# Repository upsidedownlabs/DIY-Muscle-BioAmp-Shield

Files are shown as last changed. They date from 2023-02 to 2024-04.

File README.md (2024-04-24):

# Muscle BioAmp Shield

 


[]()



Muscle BioAmp Shield is an all-in-one Arduino Uno ElectroMyography (EMG) shield for learning neuroscience with ease. It is a DIY Electrophysiology/NeuroScience shield inspired from Back Yard Brains (BYB) Muscle Spiker shield and provides similar features like hobby servo output, user buttons, LED Bar, Audio output, and battery input. It is perfect for beginners as they can easily stack it on top of Arduino Uno to record, visualize and listen to their muscle signals to make amazing projects in the domain of Human-Computer Interface (HCI).

## Features & Specifications

Muscle BioAmp Shield comes with various plug-and-play options so you can connect hundreds of extension boards like OLED screens, character displays, accelerometers, and servo controllers to name just a few using the STEMMA I2C interface. You also get STEMMA digital and STEMMA analog ports. On STEMMA analog port you can connect additional [BioAmp EXG Pill](https://github.com/upsidedownlabs/BioAmp-EXG-Pill) or any other sensor with analog output. On STEMMA digital port you can connect any digital sensor or actuator of your choice.

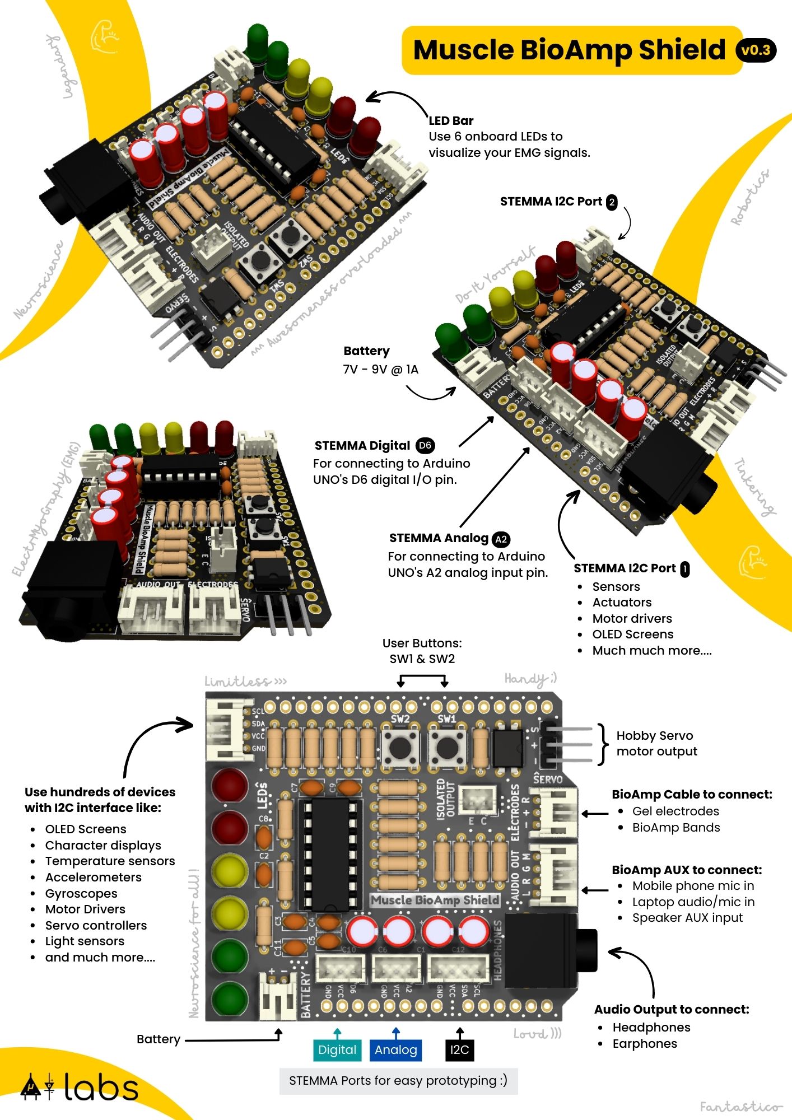
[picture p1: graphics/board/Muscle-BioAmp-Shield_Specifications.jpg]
Muscle BioAmp Shield Specifications


## Assembly
You can get your own Muscle BioAmp Shield bag of parts from [our store](https://store.upsidedownlabs.tech/product/muscle-bioamp-shield-v0-3/) or [Tindie](www.tindie.com/products/upsidedownlabs/muscle-bioamp-shield-v03-arduino-shield-for-emg/) and for assembling your shield you can take a look at [this interactive BOM](https://upsidedownlabs.github.io/DIY-Muscle-BioAmp-Shield/ibom.html) or the step by step guide below. 

| Step 1 - Bare board | Step 2 - 1M Resistors | Step 3 - 330R Resistors| 
| :----: | :----: | :----: |
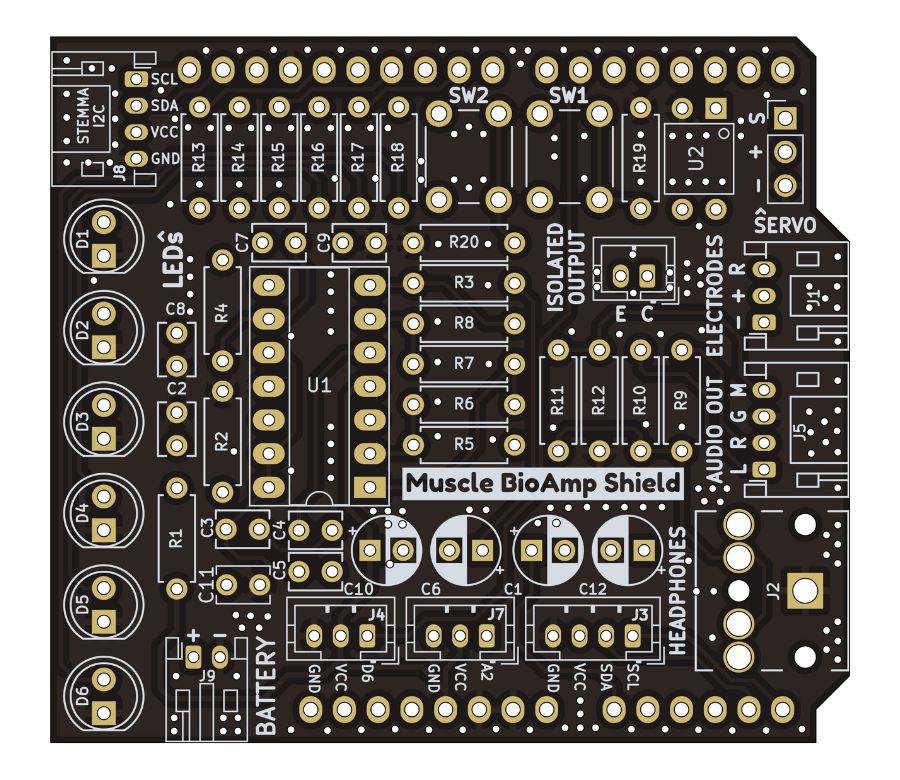
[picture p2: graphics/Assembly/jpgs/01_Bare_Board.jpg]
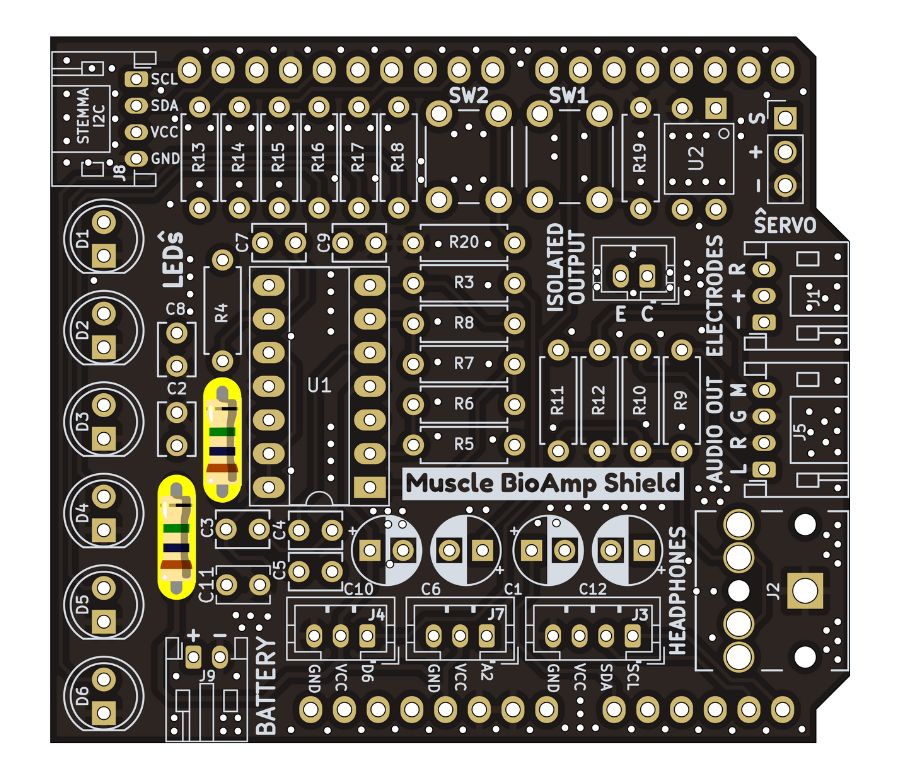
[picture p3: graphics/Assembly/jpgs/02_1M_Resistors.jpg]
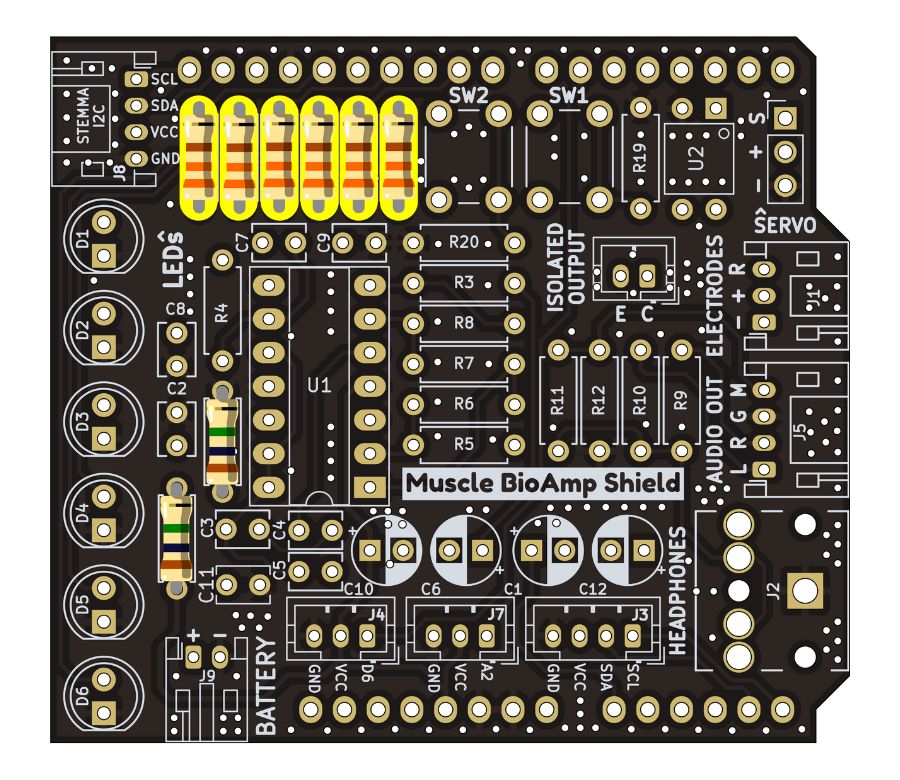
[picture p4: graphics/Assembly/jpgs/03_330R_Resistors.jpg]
| |||

| Step 4 - 10K Resistors | Step 5 - 22K Resistors | Step 6 - 1K Resistors| 
| :----: | :----: | :----: |
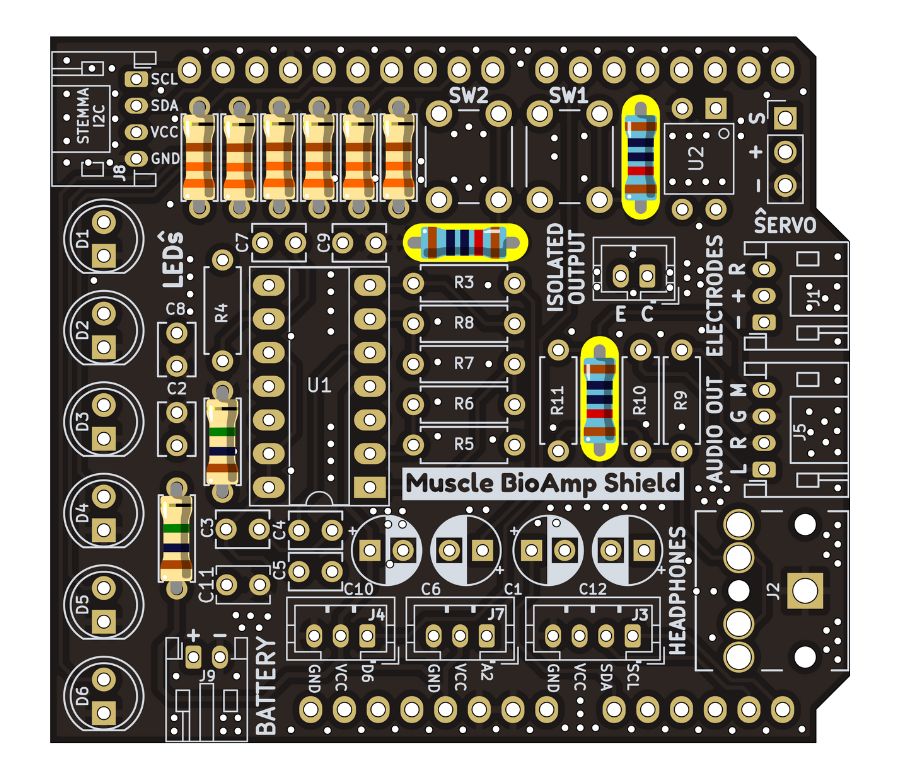
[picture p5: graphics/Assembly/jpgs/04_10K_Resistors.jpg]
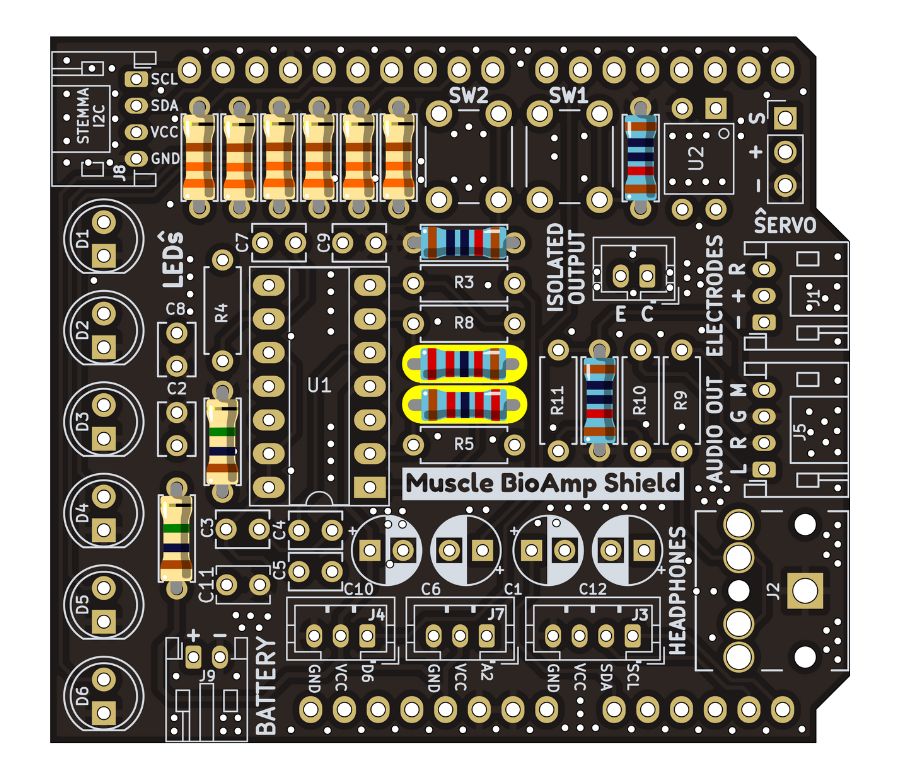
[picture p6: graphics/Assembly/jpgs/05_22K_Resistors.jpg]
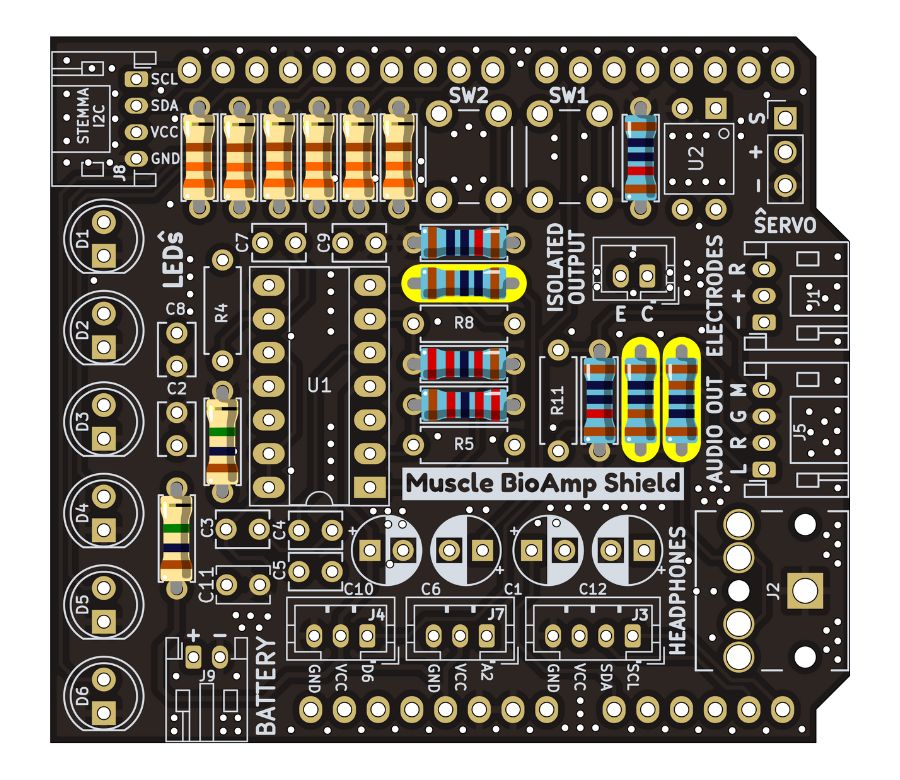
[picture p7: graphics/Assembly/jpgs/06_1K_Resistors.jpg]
| |||

| Step 7 - 220K Resistors | Step 8 - 1nF Capacitors | Step 9 - 100nF Capacitors| 
| :----: | :----: | :----: |
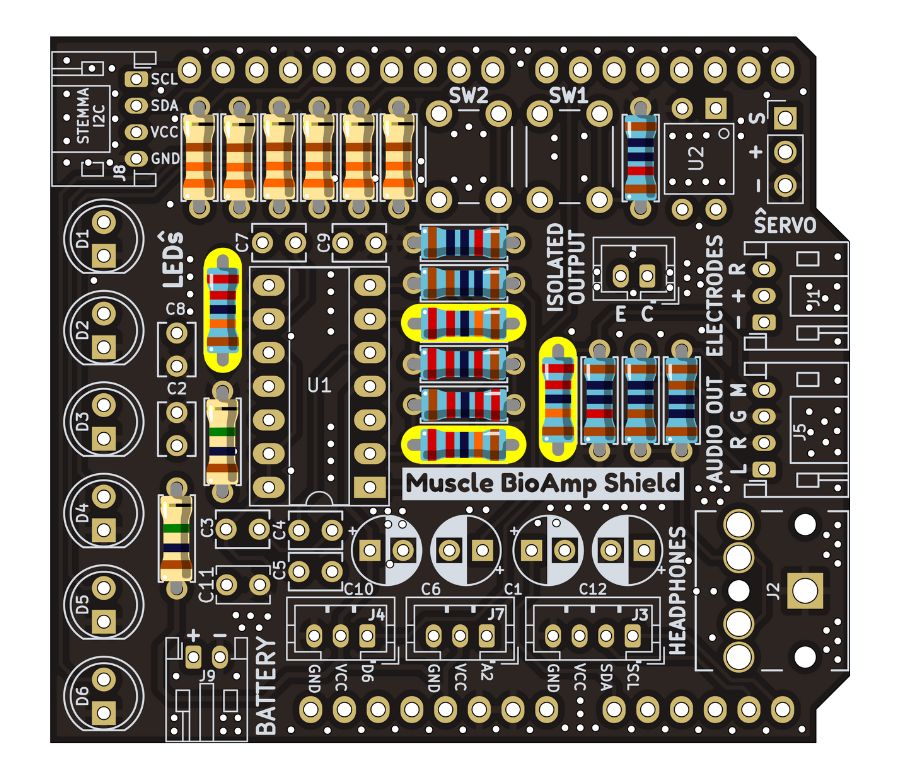
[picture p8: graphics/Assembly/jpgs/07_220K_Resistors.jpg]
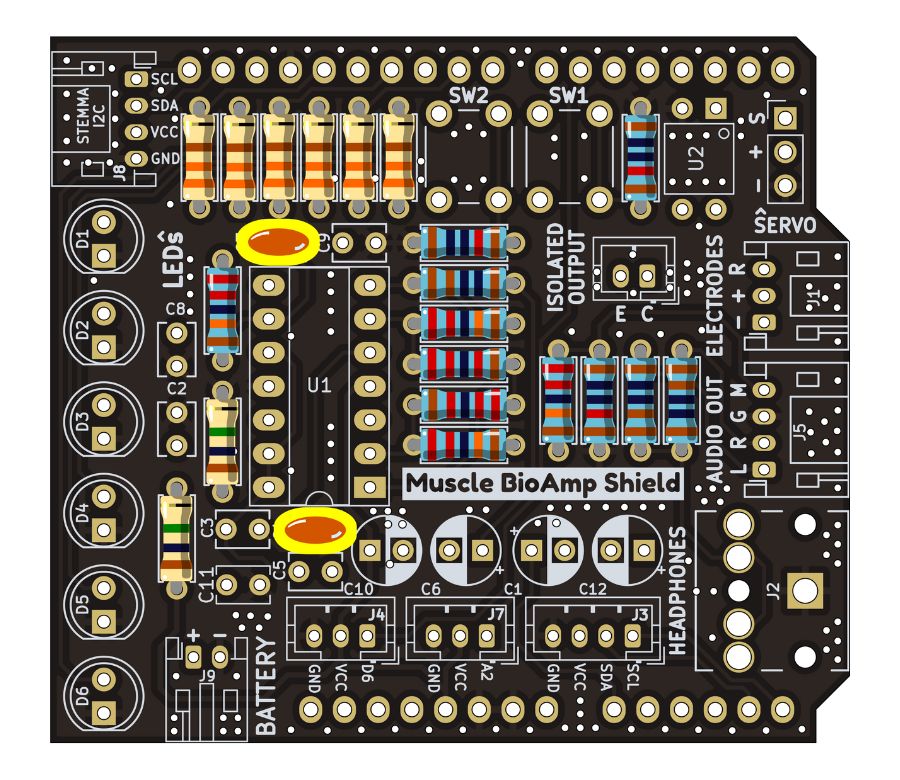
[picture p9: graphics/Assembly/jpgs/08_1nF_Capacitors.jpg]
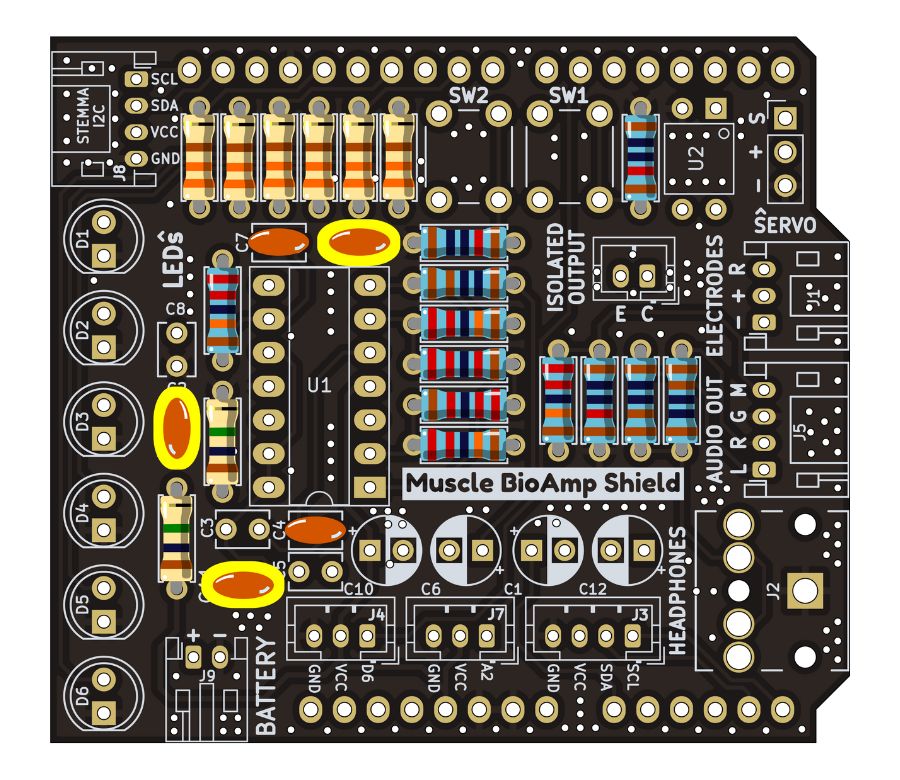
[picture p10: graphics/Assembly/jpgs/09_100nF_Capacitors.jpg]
| |||

| Step 10 - 100pF Capacitors | Step 11 - Servo Header Pin | Step 12 - Buttons| 
| :----: | :----: | :----: |
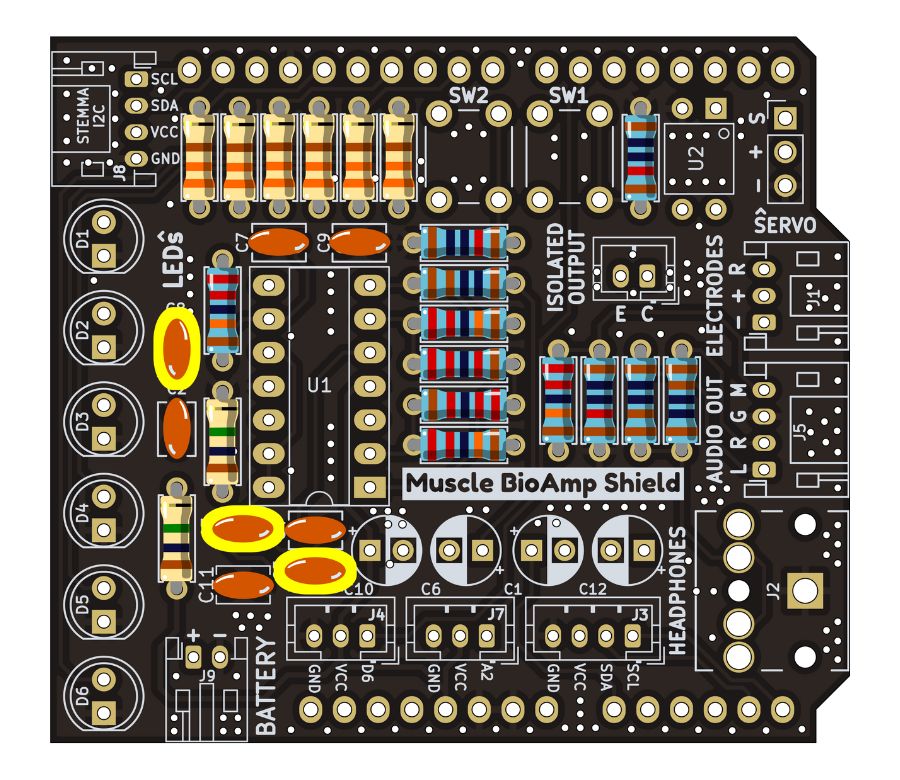
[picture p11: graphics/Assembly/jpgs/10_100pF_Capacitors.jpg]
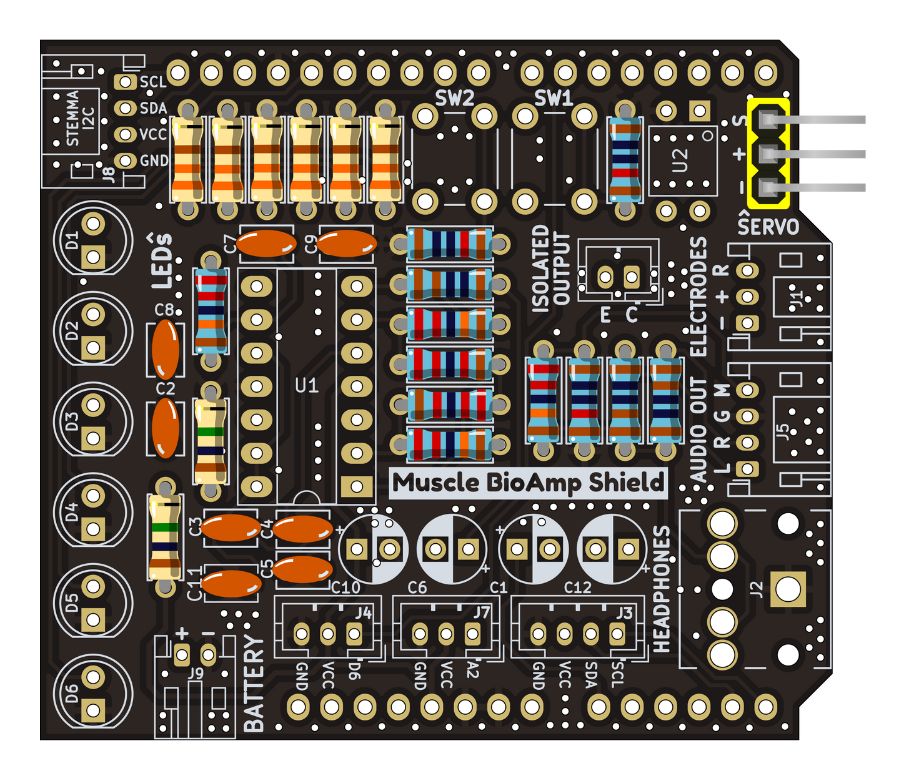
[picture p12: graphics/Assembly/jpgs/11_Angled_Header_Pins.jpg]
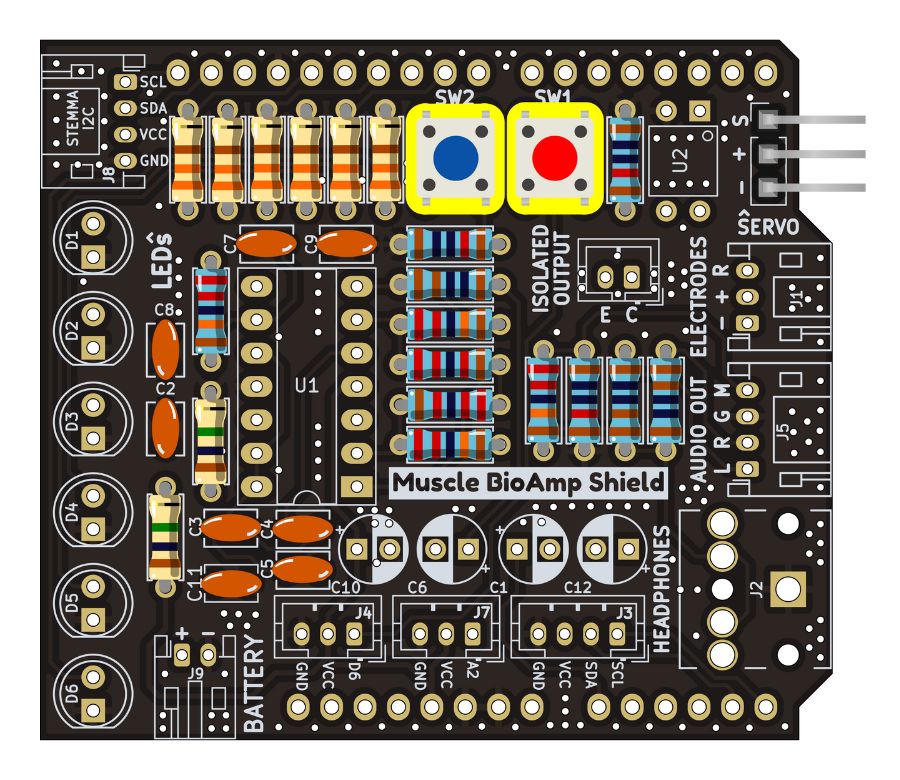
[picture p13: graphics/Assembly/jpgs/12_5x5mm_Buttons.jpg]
| |||

| Step 13 - Optoisolator | Step 14 - Angled JST Connectors | Step 15 - Straight JST Connectors| 
| :----: | :----: | :----: |
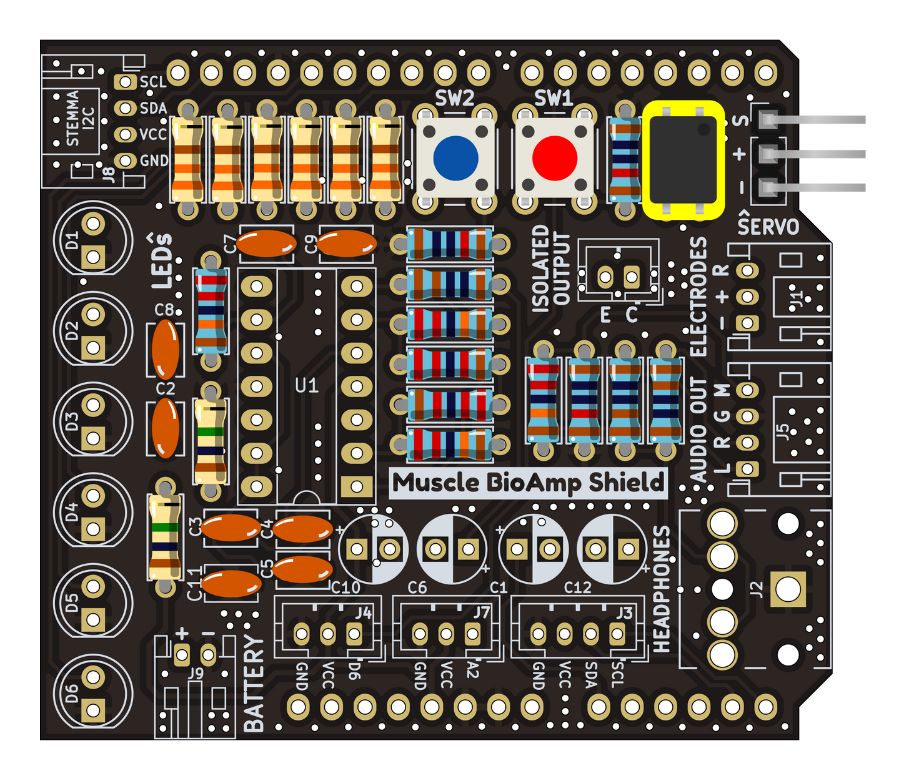
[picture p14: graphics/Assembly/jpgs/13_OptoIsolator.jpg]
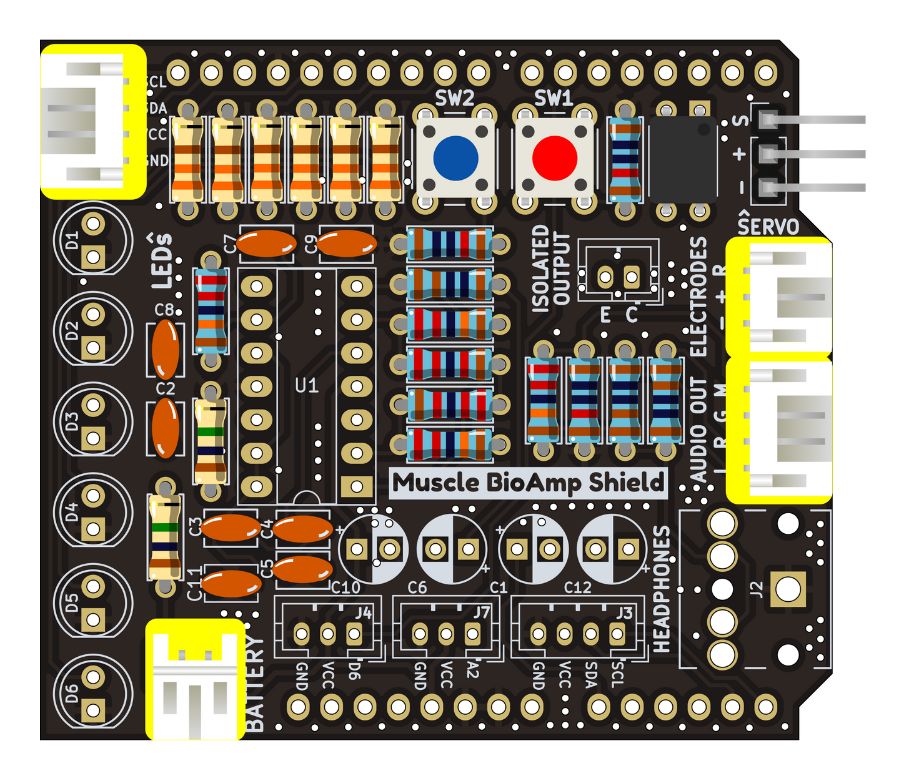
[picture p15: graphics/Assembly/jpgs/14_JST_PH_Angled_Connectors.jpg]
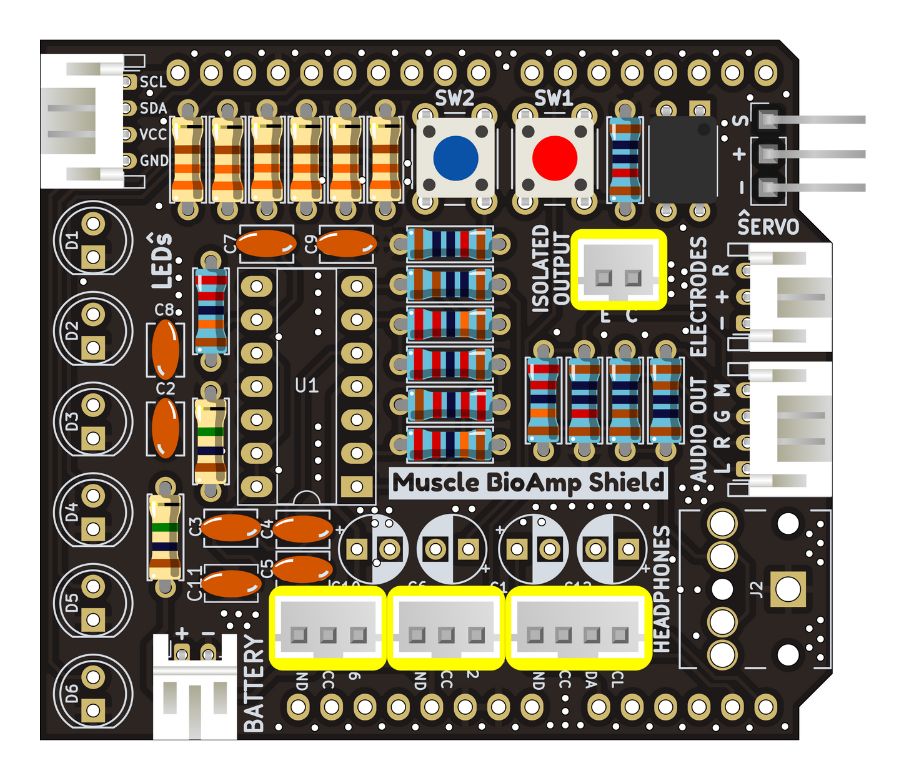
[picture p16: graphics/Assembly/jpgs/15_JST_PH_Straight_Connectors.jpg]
| |||

| Step 16 - IC Socket | Step 17 - IC | Step 18 - LEDs| 
| :----: | :----: | :----: |
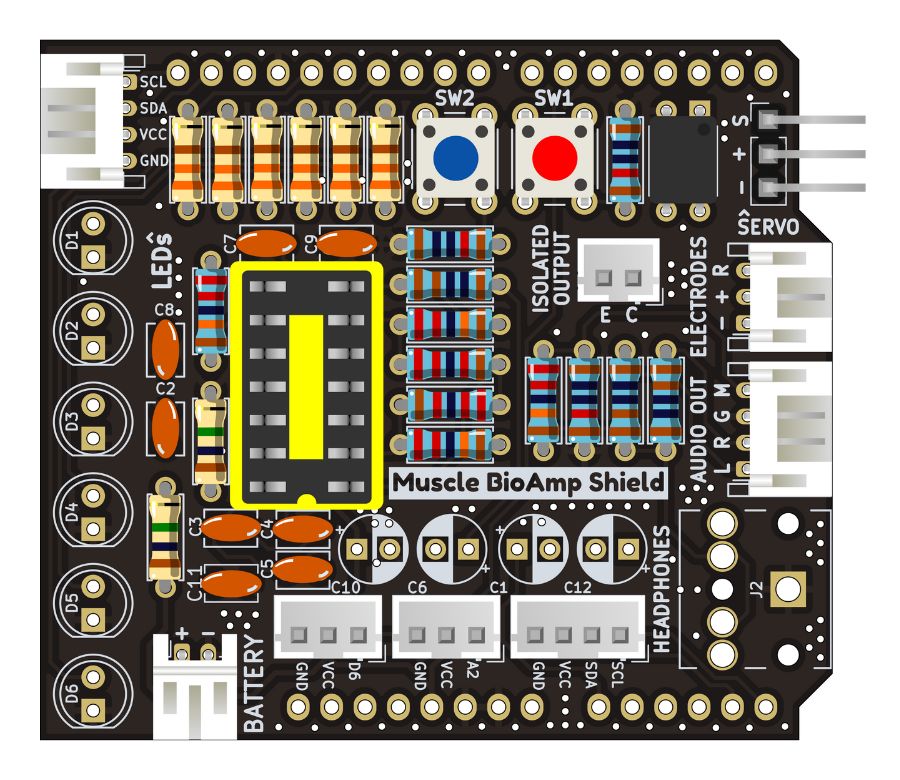
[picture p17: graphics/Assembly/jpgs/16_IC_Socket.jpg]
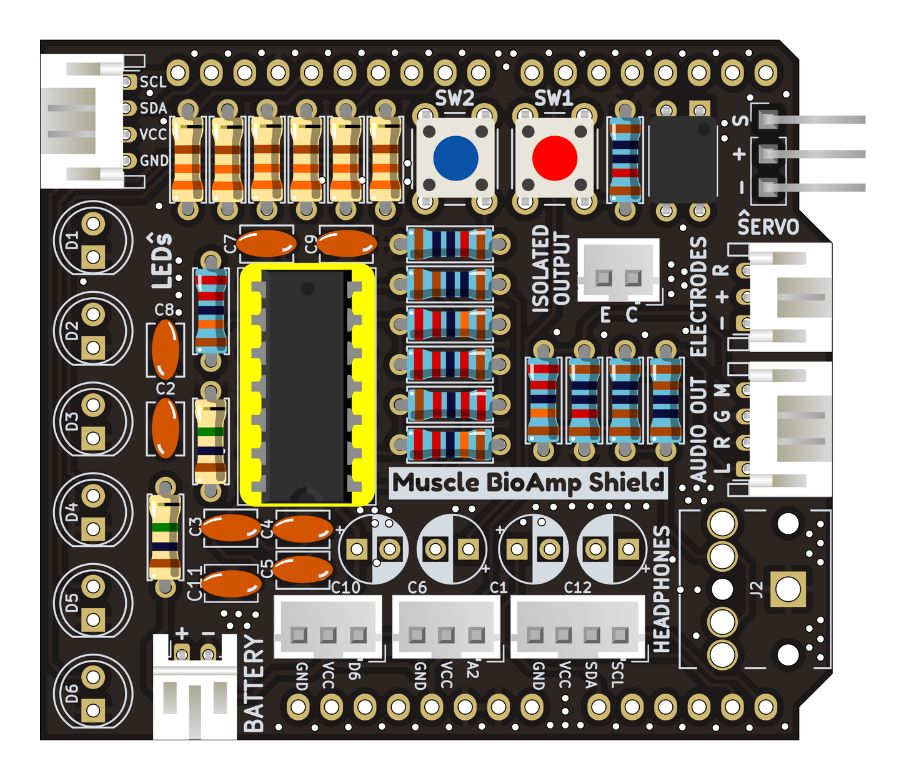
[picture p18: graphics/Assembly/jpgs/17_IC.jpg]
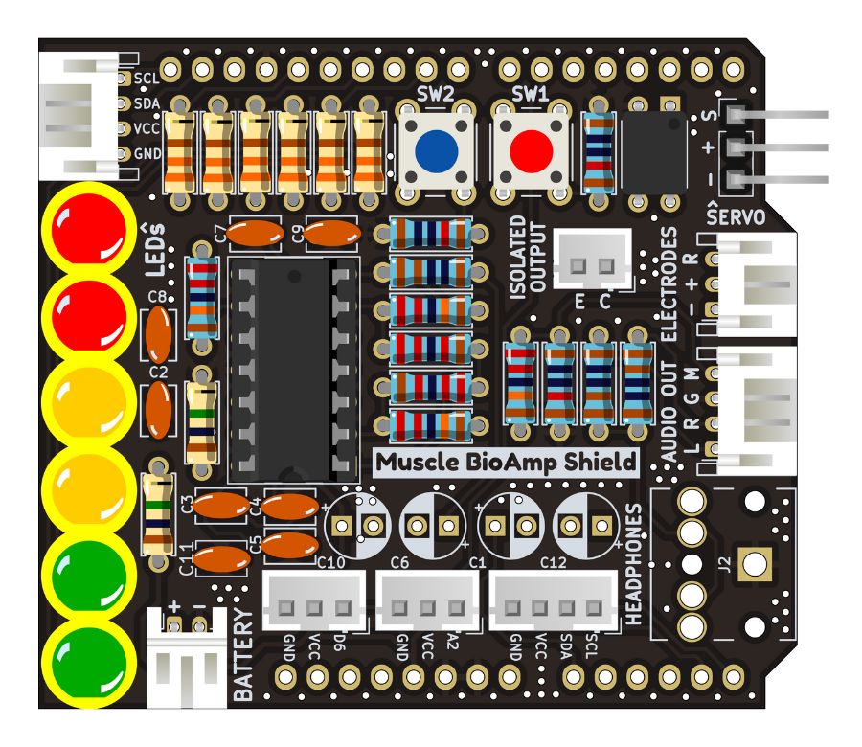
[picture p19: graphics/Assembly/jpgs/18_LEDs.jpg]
| |||

| Step 19 - 3.5mm Headphone Jack | Step 20 - 2.2uF Capacitor | Step 21 - 1uF Capacitor| 
| :----: | :----: | :----: |
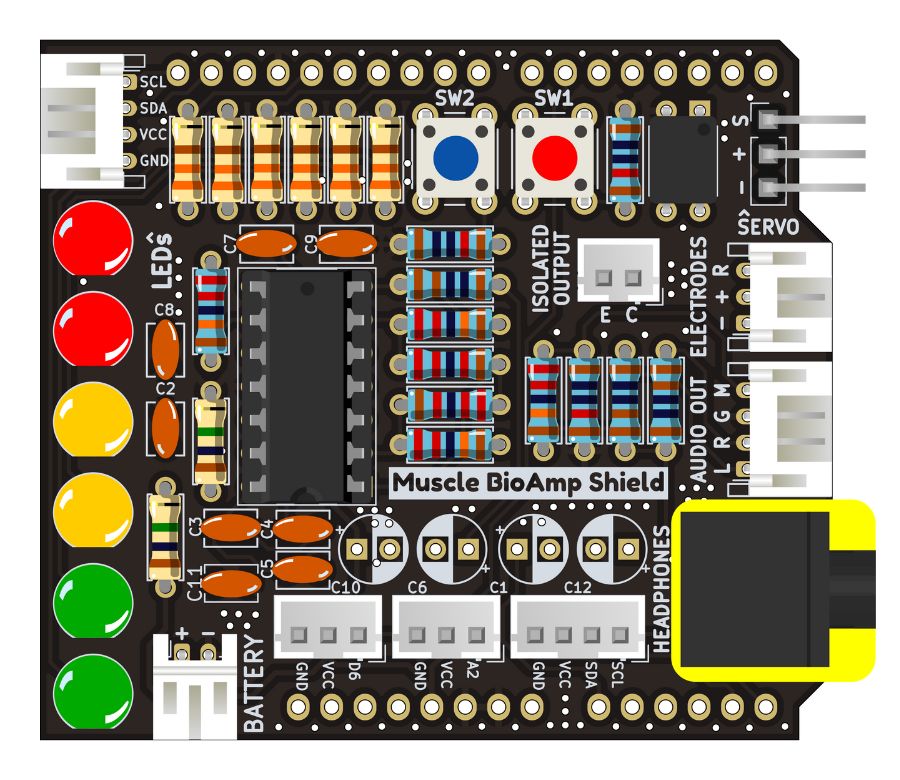
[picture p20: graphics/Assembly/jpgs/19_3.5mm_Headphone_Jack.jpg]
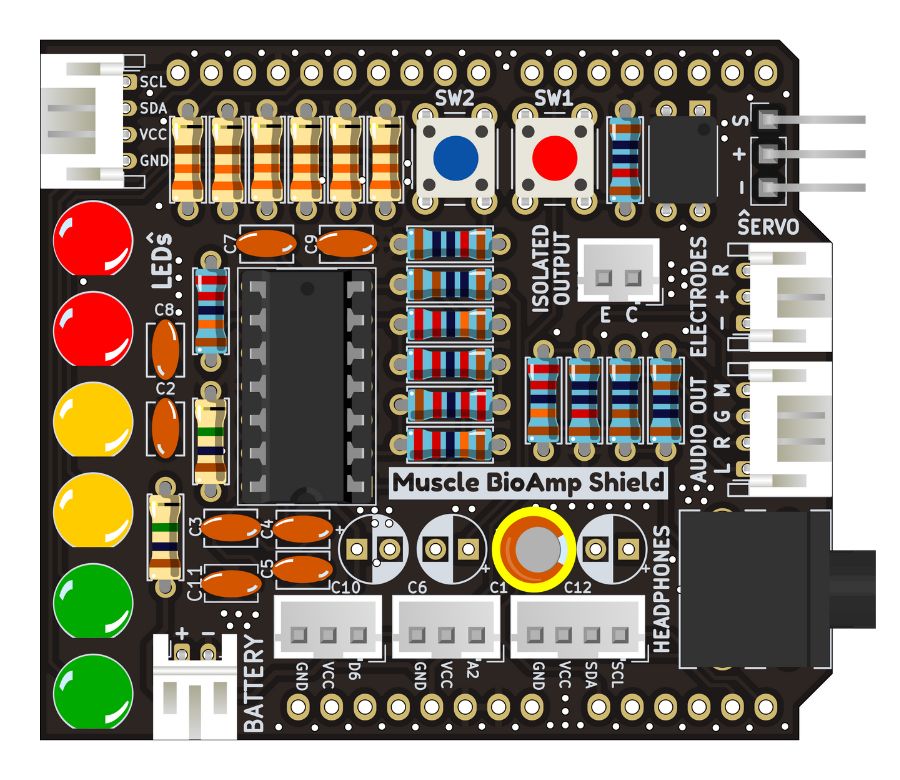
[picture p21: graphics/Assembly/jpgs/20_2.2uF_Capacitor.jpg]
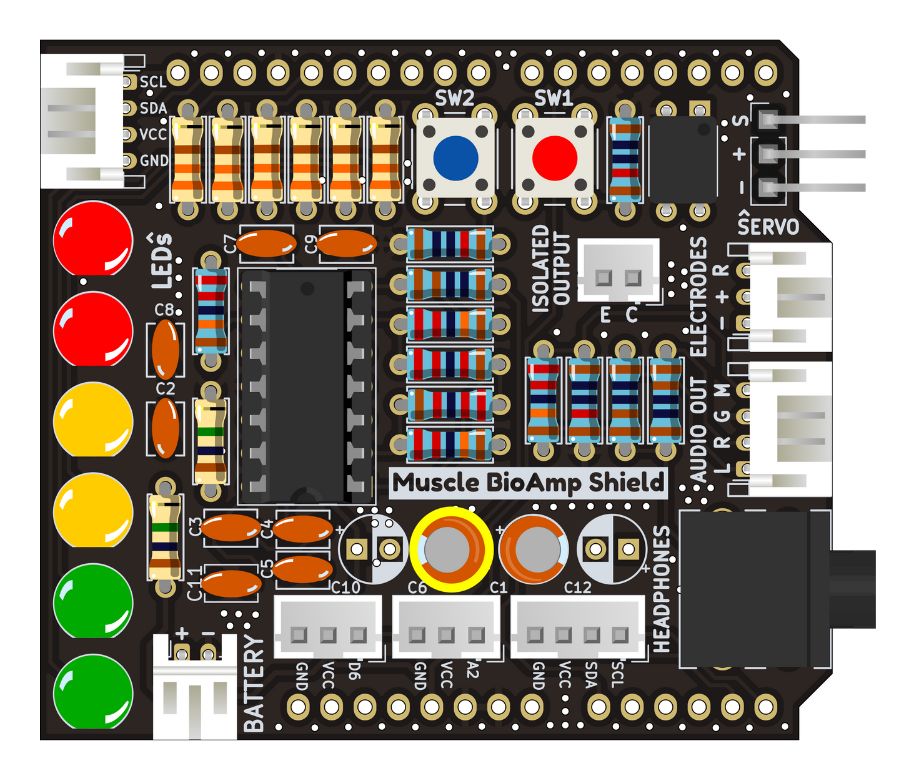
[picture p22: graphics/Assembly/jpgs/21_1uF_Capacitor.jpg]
| |||

| Step 22 - 470uF Capacitors | Step 23 - Shield Header Pins | Step 24 - Shield Ready| 
| :----: | :----: | :----: |
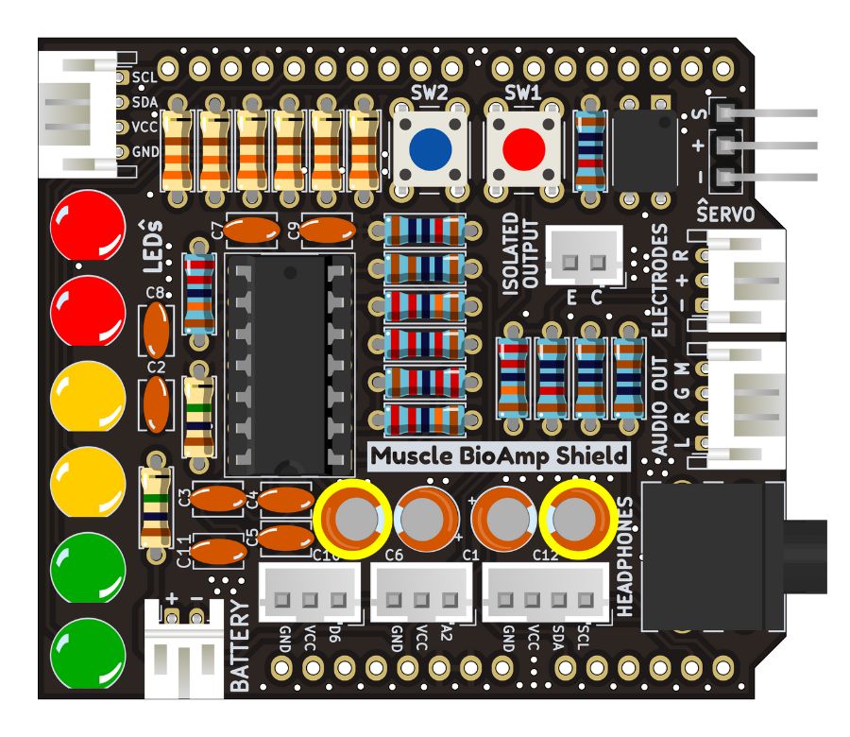
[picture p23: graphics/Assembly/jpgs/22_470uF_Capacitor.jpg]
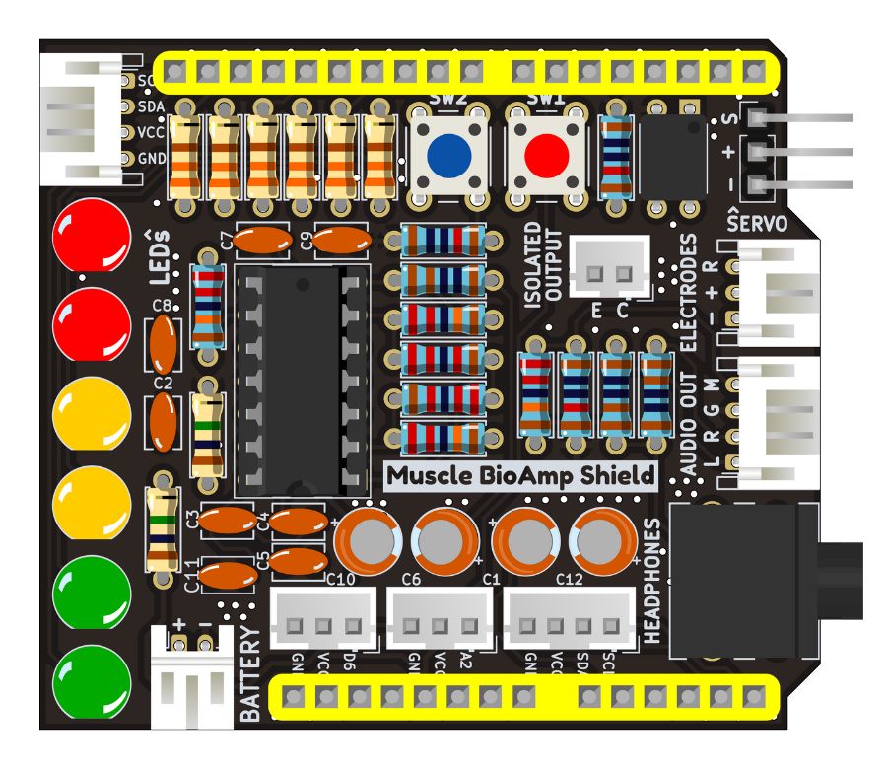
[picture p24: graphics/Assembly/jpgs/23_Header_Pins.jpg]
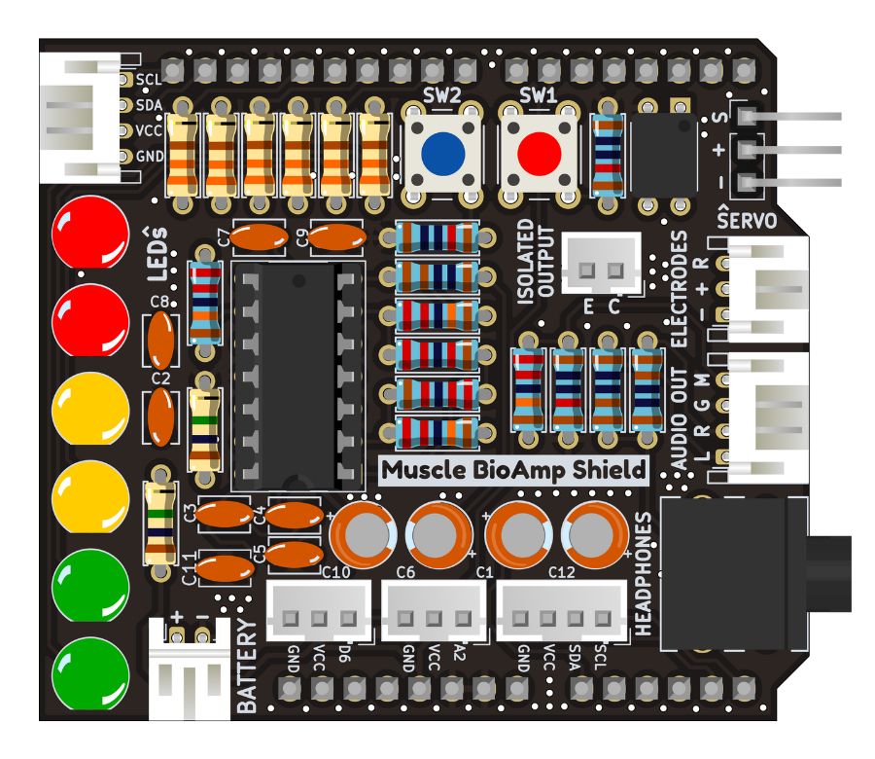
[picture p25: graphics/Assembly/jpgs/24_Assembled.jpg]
| |||

## What's in the kit

Muscle BioAmp Shield comes in two variants: Pre-Assembled and DIY (Do-It-Yourself). You can order any of the two variants as per your requirement.

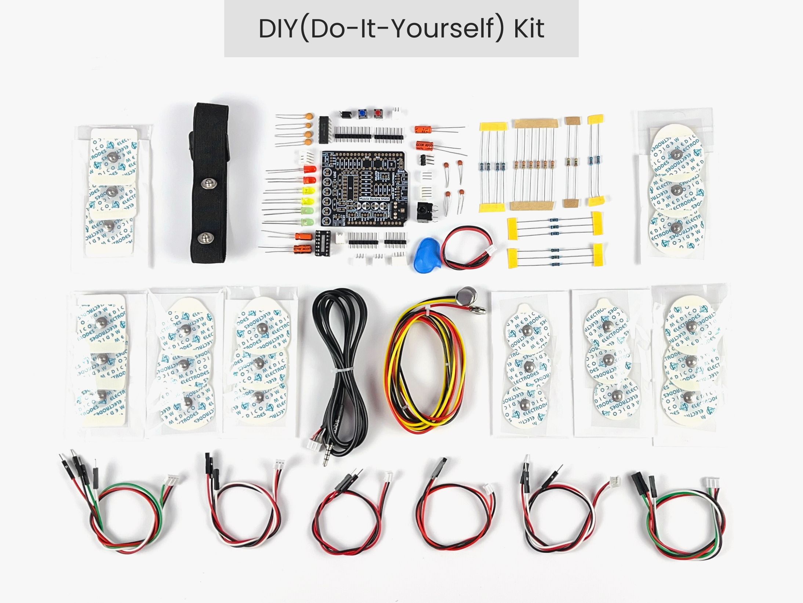
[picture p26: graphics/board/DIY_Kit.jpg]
DIY Kit

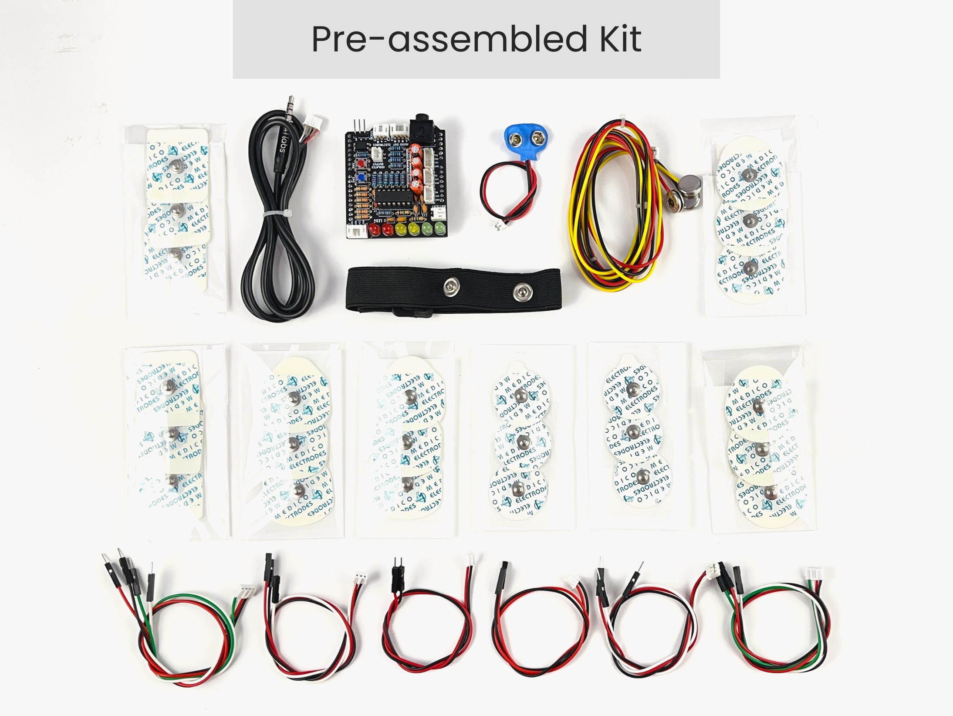
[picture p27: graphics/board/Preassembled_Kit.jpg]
Pre-Assembled Kit


## Hardware

Muscle BioAmp Shield has been created using KiCad and all the design files can be found under [hardware](hardware/) folder, including [Interactive BOM](https://upsidedownlabs.github.io/DIY-Muscle-BioAmp-Shield/ibom.html) file. Images below shows a quick overview of the hardware design.

| PCB front | PCB back |
| :-------: | :--------: |
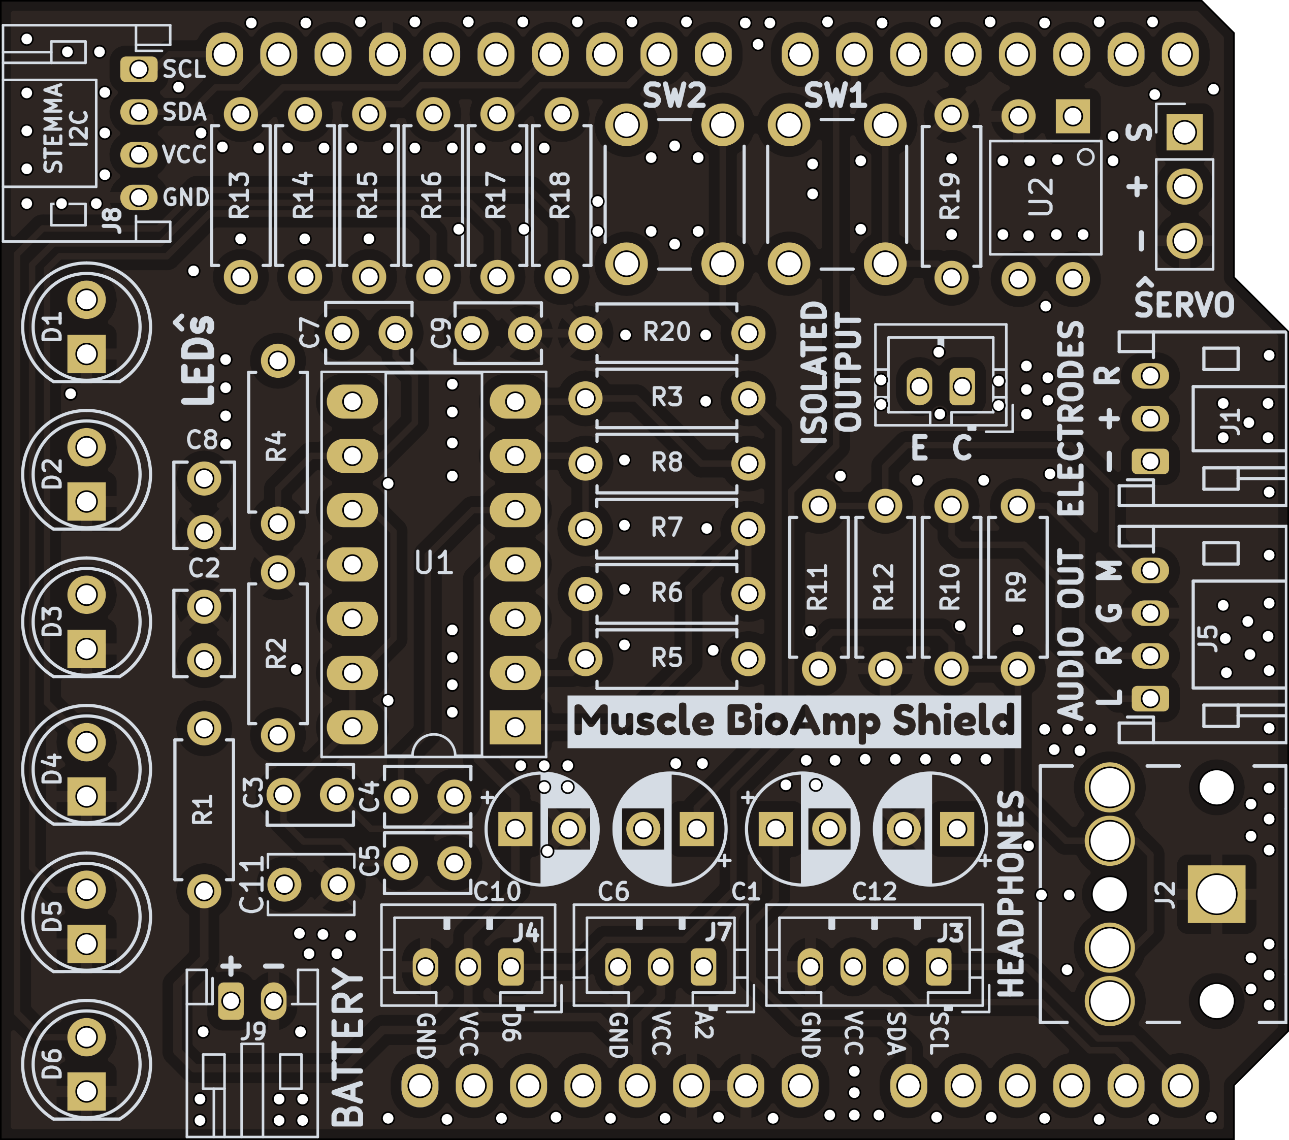
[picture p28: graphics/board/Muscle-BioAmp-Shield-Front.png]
Muscle BioAmp Shield
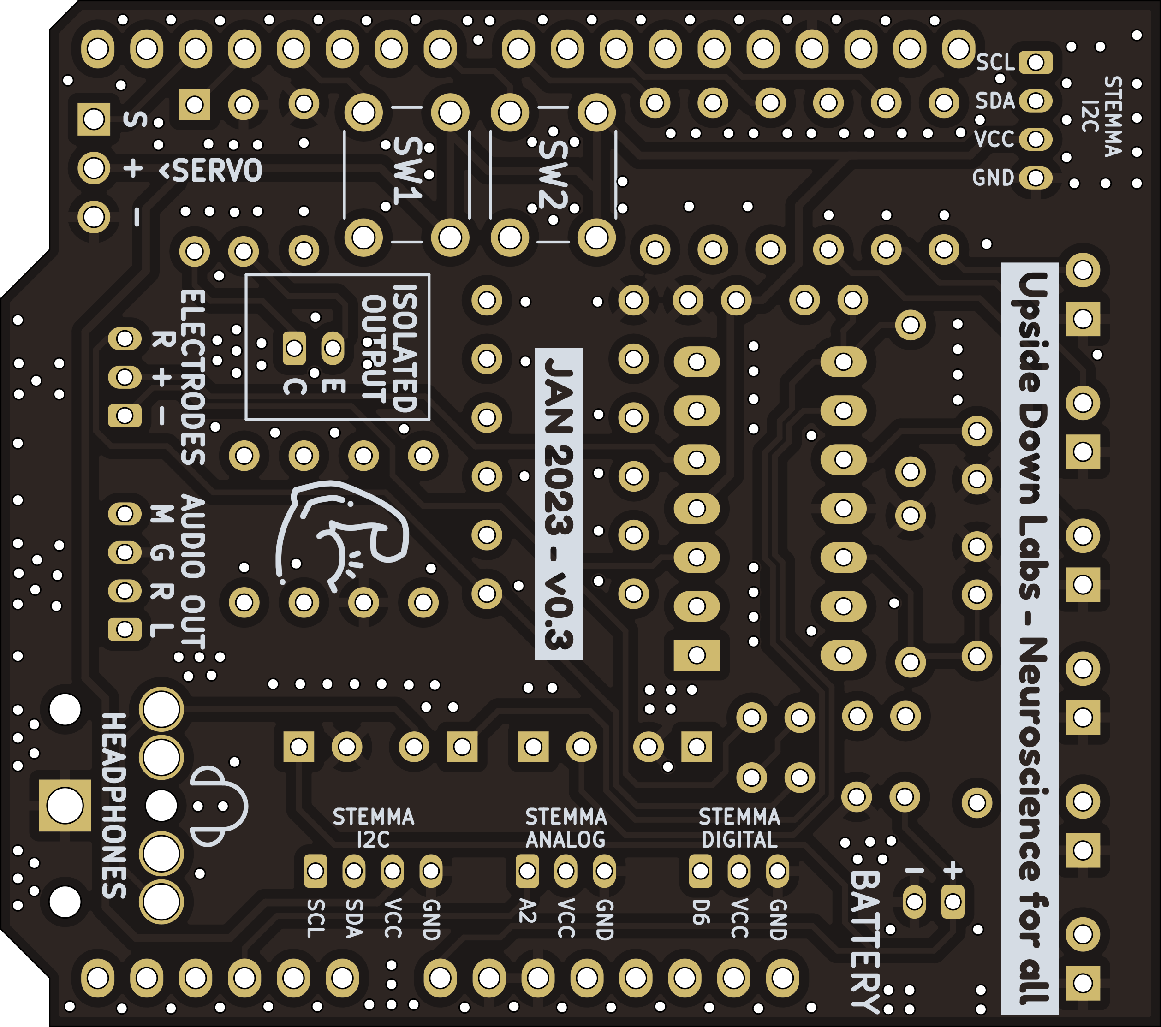
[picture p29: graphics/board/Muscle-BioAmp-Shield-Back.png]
Muscle BioAmp Shield
|  |  |

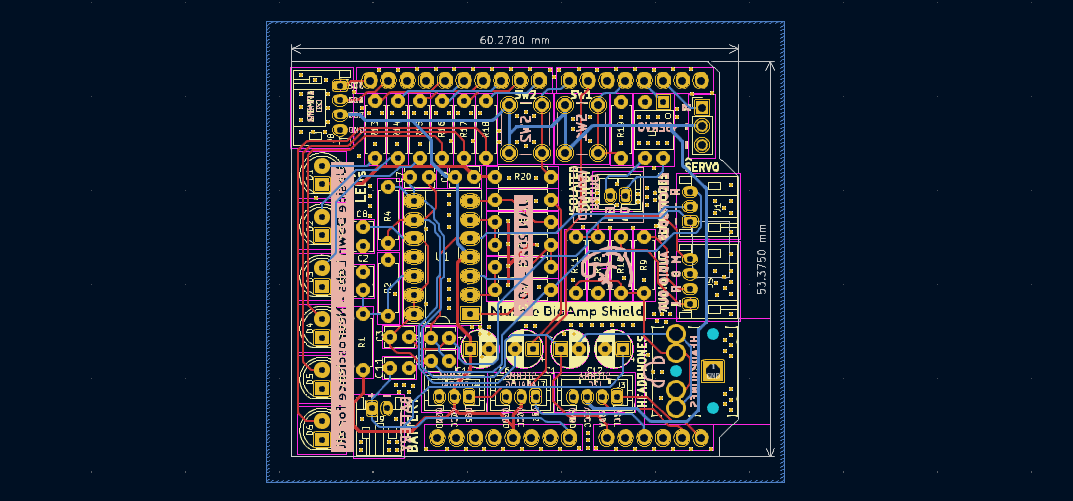
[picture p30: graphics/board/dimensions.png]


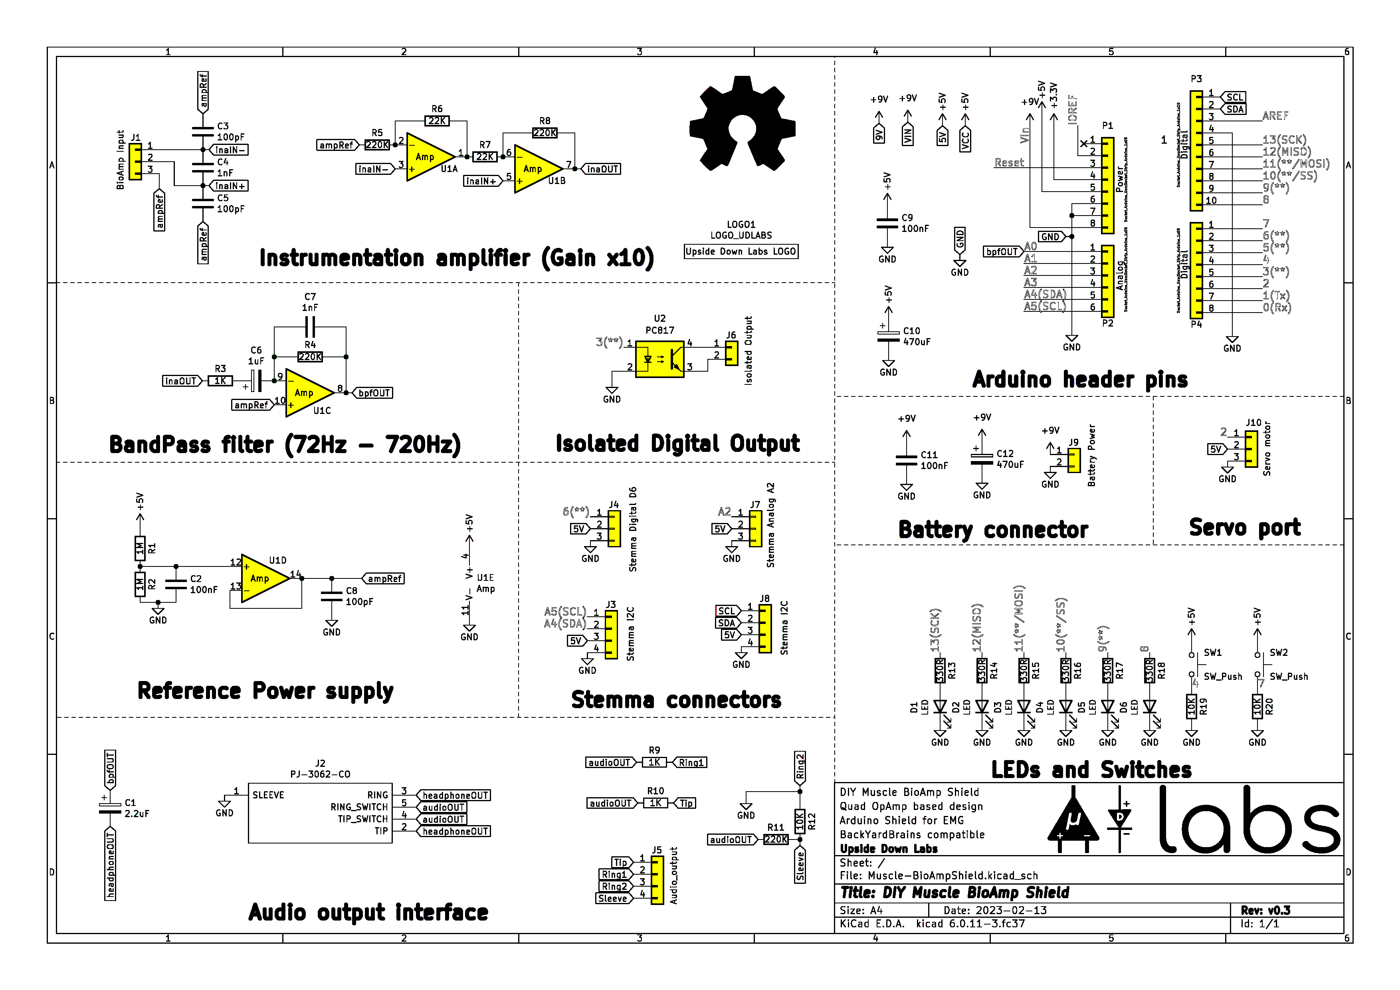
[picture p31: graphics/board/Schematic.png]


## License

#### Hardware
CERN Open Hardware License Version 2 - Strongly Reciprocal ([CERN-OHL-S-2.0](https://spdx.org/licenses/CERN-OHL-S-2.0.html)).

#### Software
MIT open source [license](http://opensource.org/licenses/MIT).

#### Documentation:
<br />This work is licensed under a <a rel="license" href="http://creativecommons.org/licenses/by/4.0/">Creative Commons Attribution 4.0 International License</a>.

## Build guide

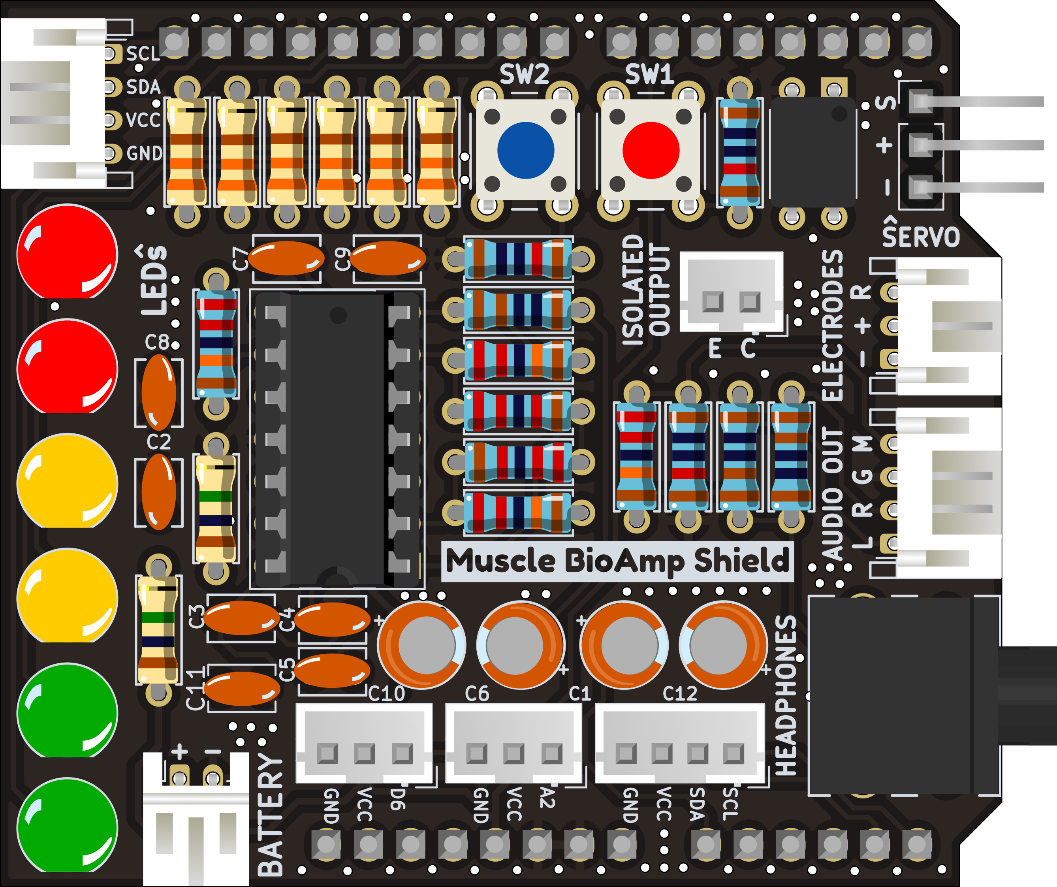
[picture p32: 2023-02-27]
graphics/Assembly/pngs/24_Assembled.png

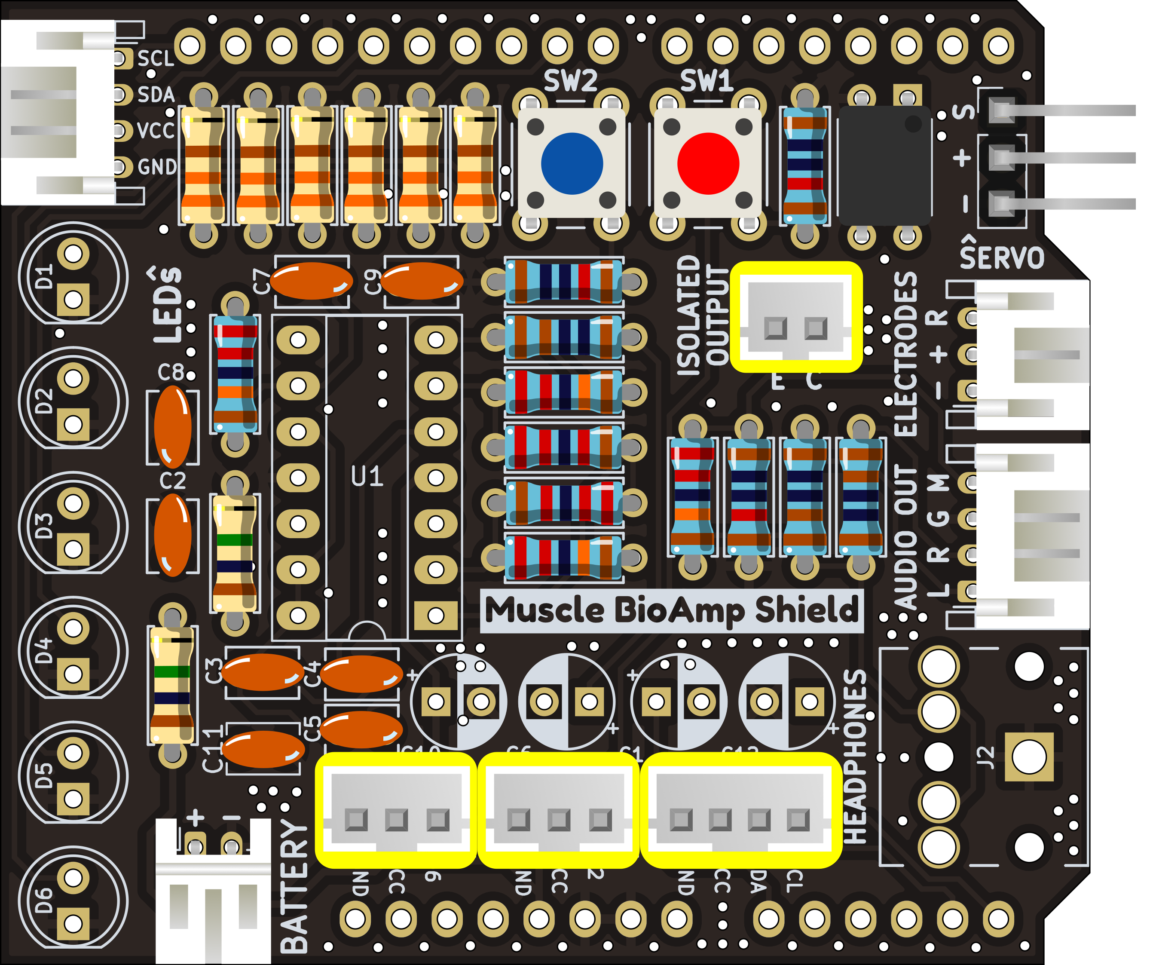
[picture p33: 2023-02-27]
graphics/Assembly/pngs/15_JST_PH_Straight_Connectors.png

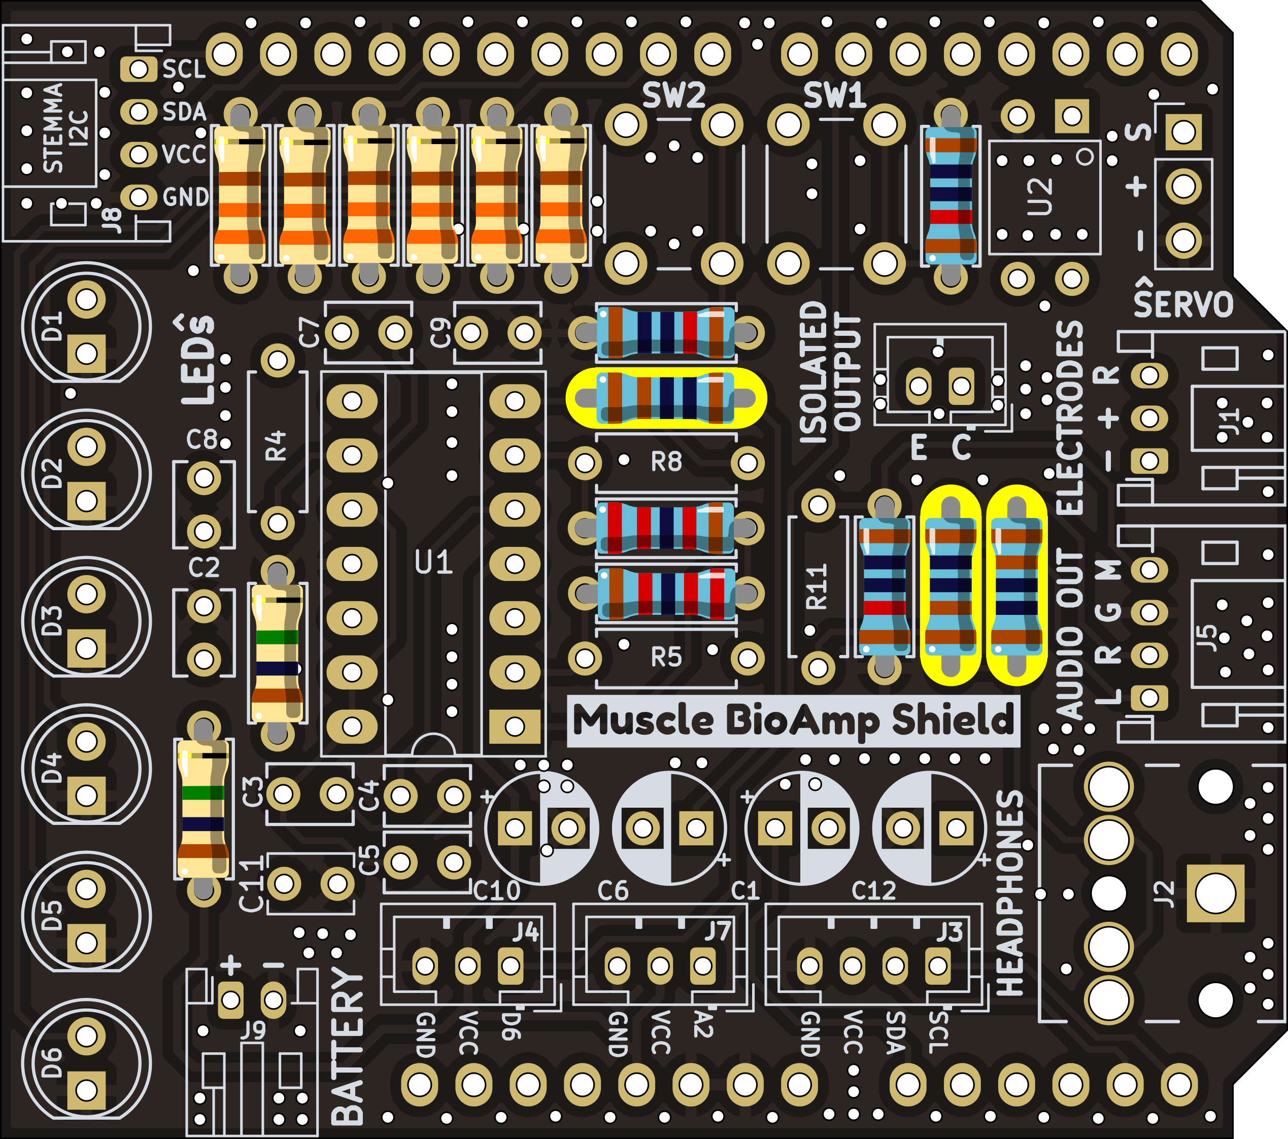
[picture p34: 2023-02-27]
graphics/Assembly/pngs/06_1K_Resistors.png

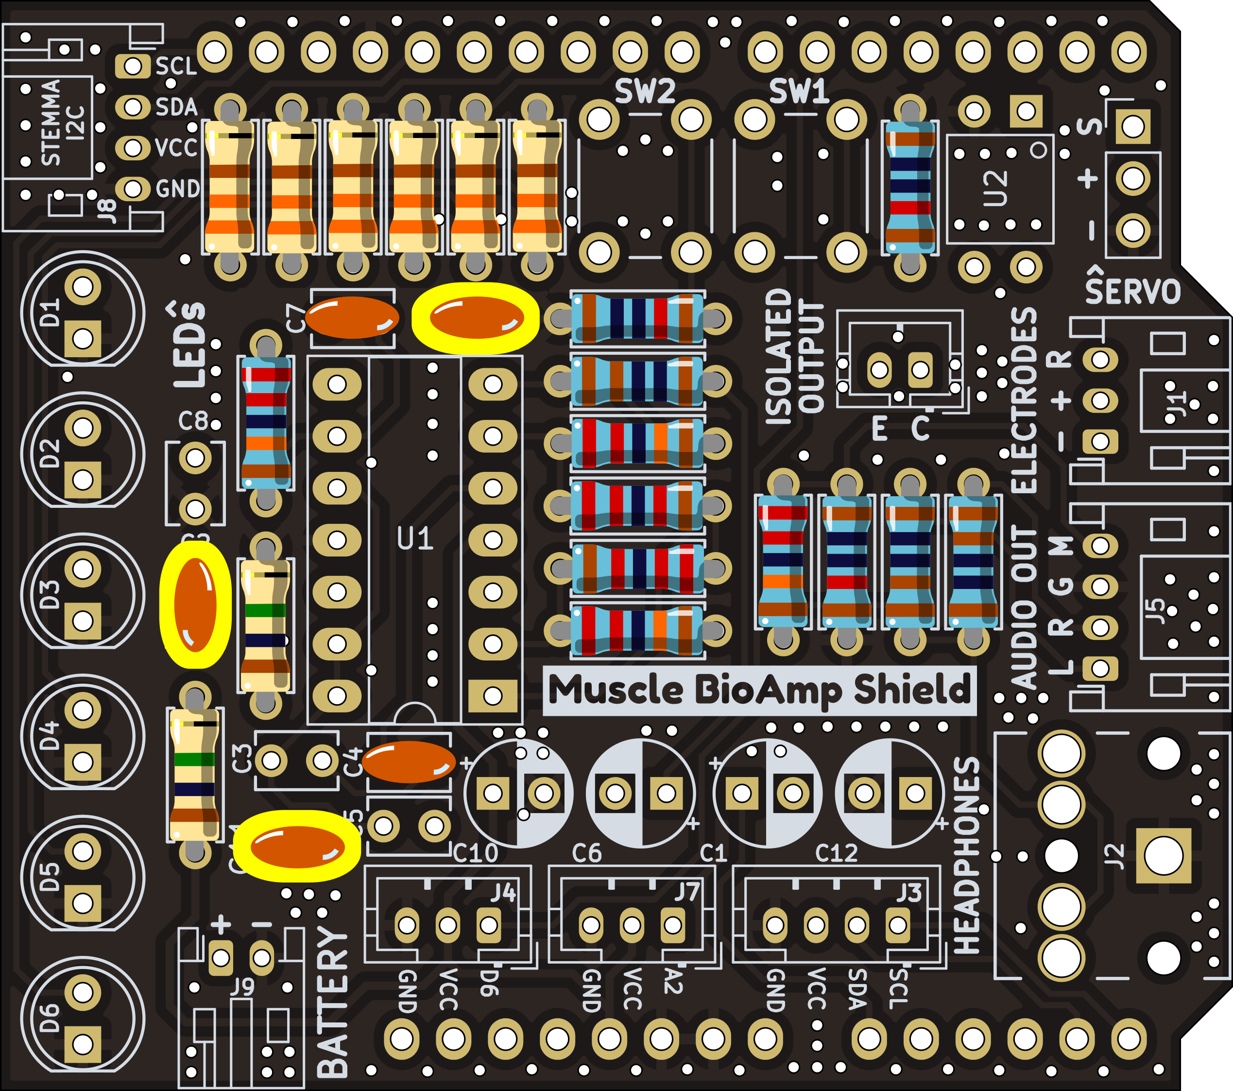
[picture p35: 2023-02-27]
graphics/Assembly/pngs/09_100nF_Capacitors.png

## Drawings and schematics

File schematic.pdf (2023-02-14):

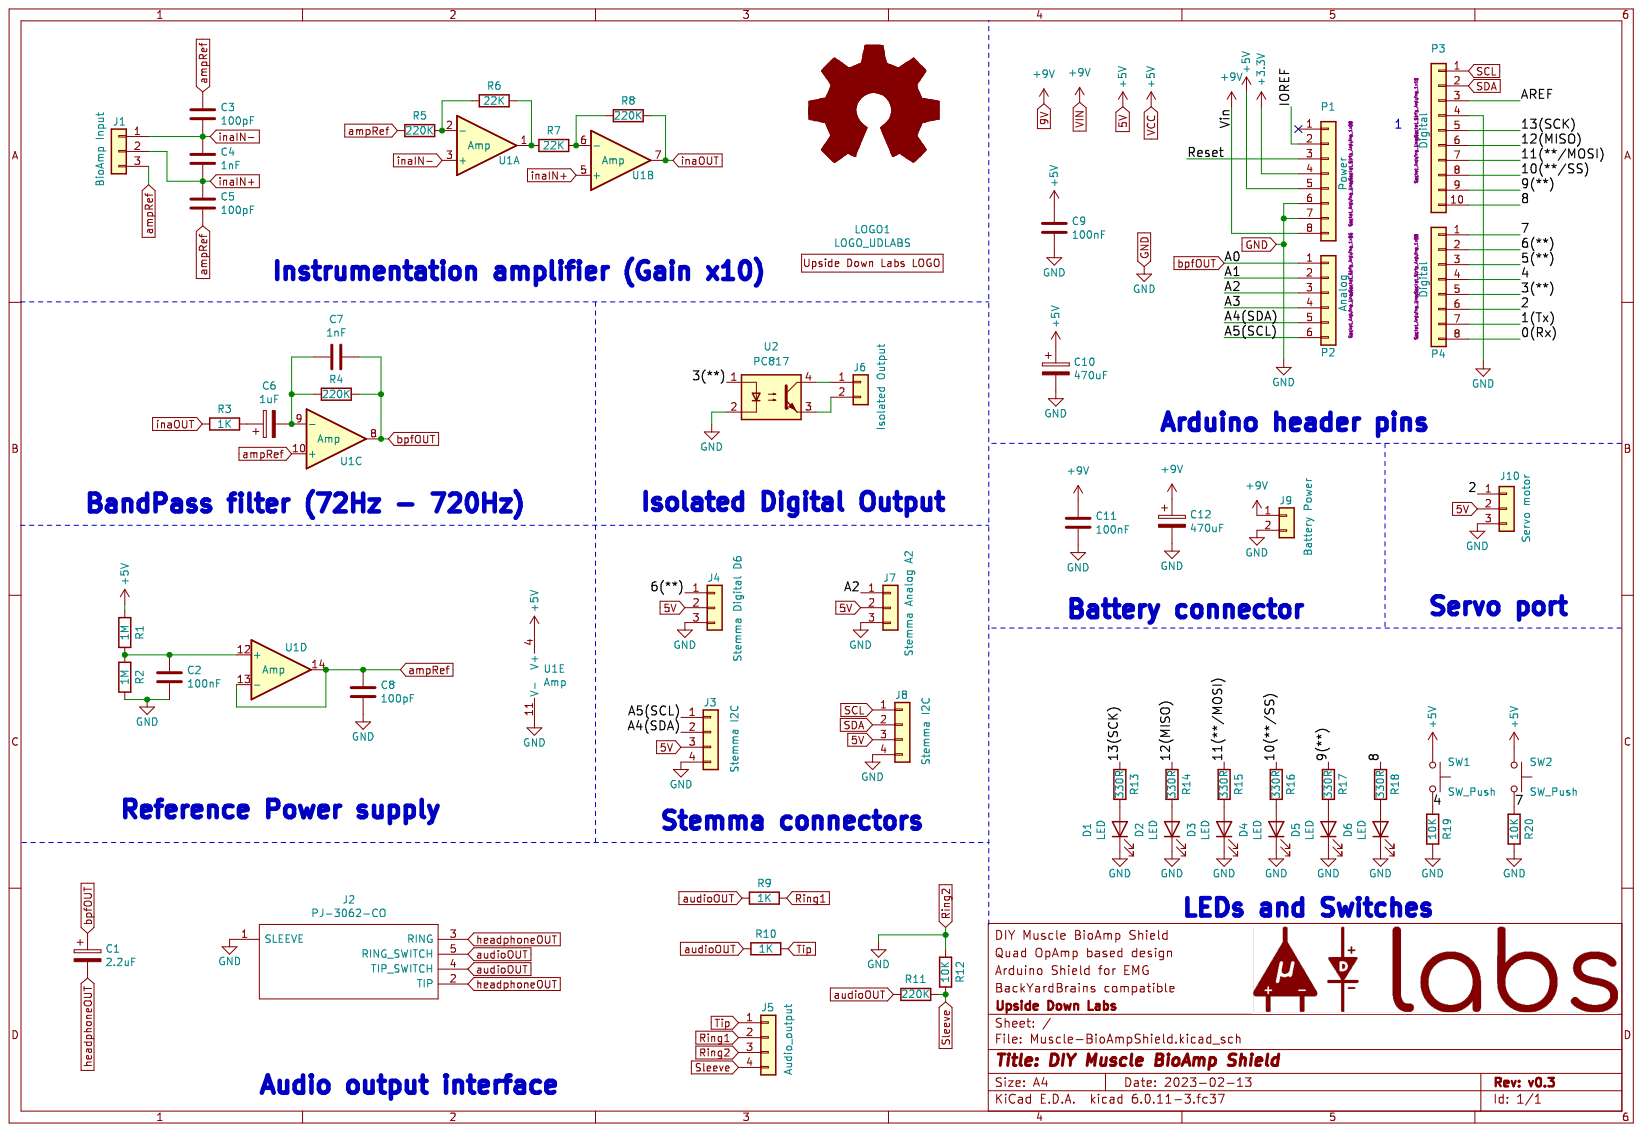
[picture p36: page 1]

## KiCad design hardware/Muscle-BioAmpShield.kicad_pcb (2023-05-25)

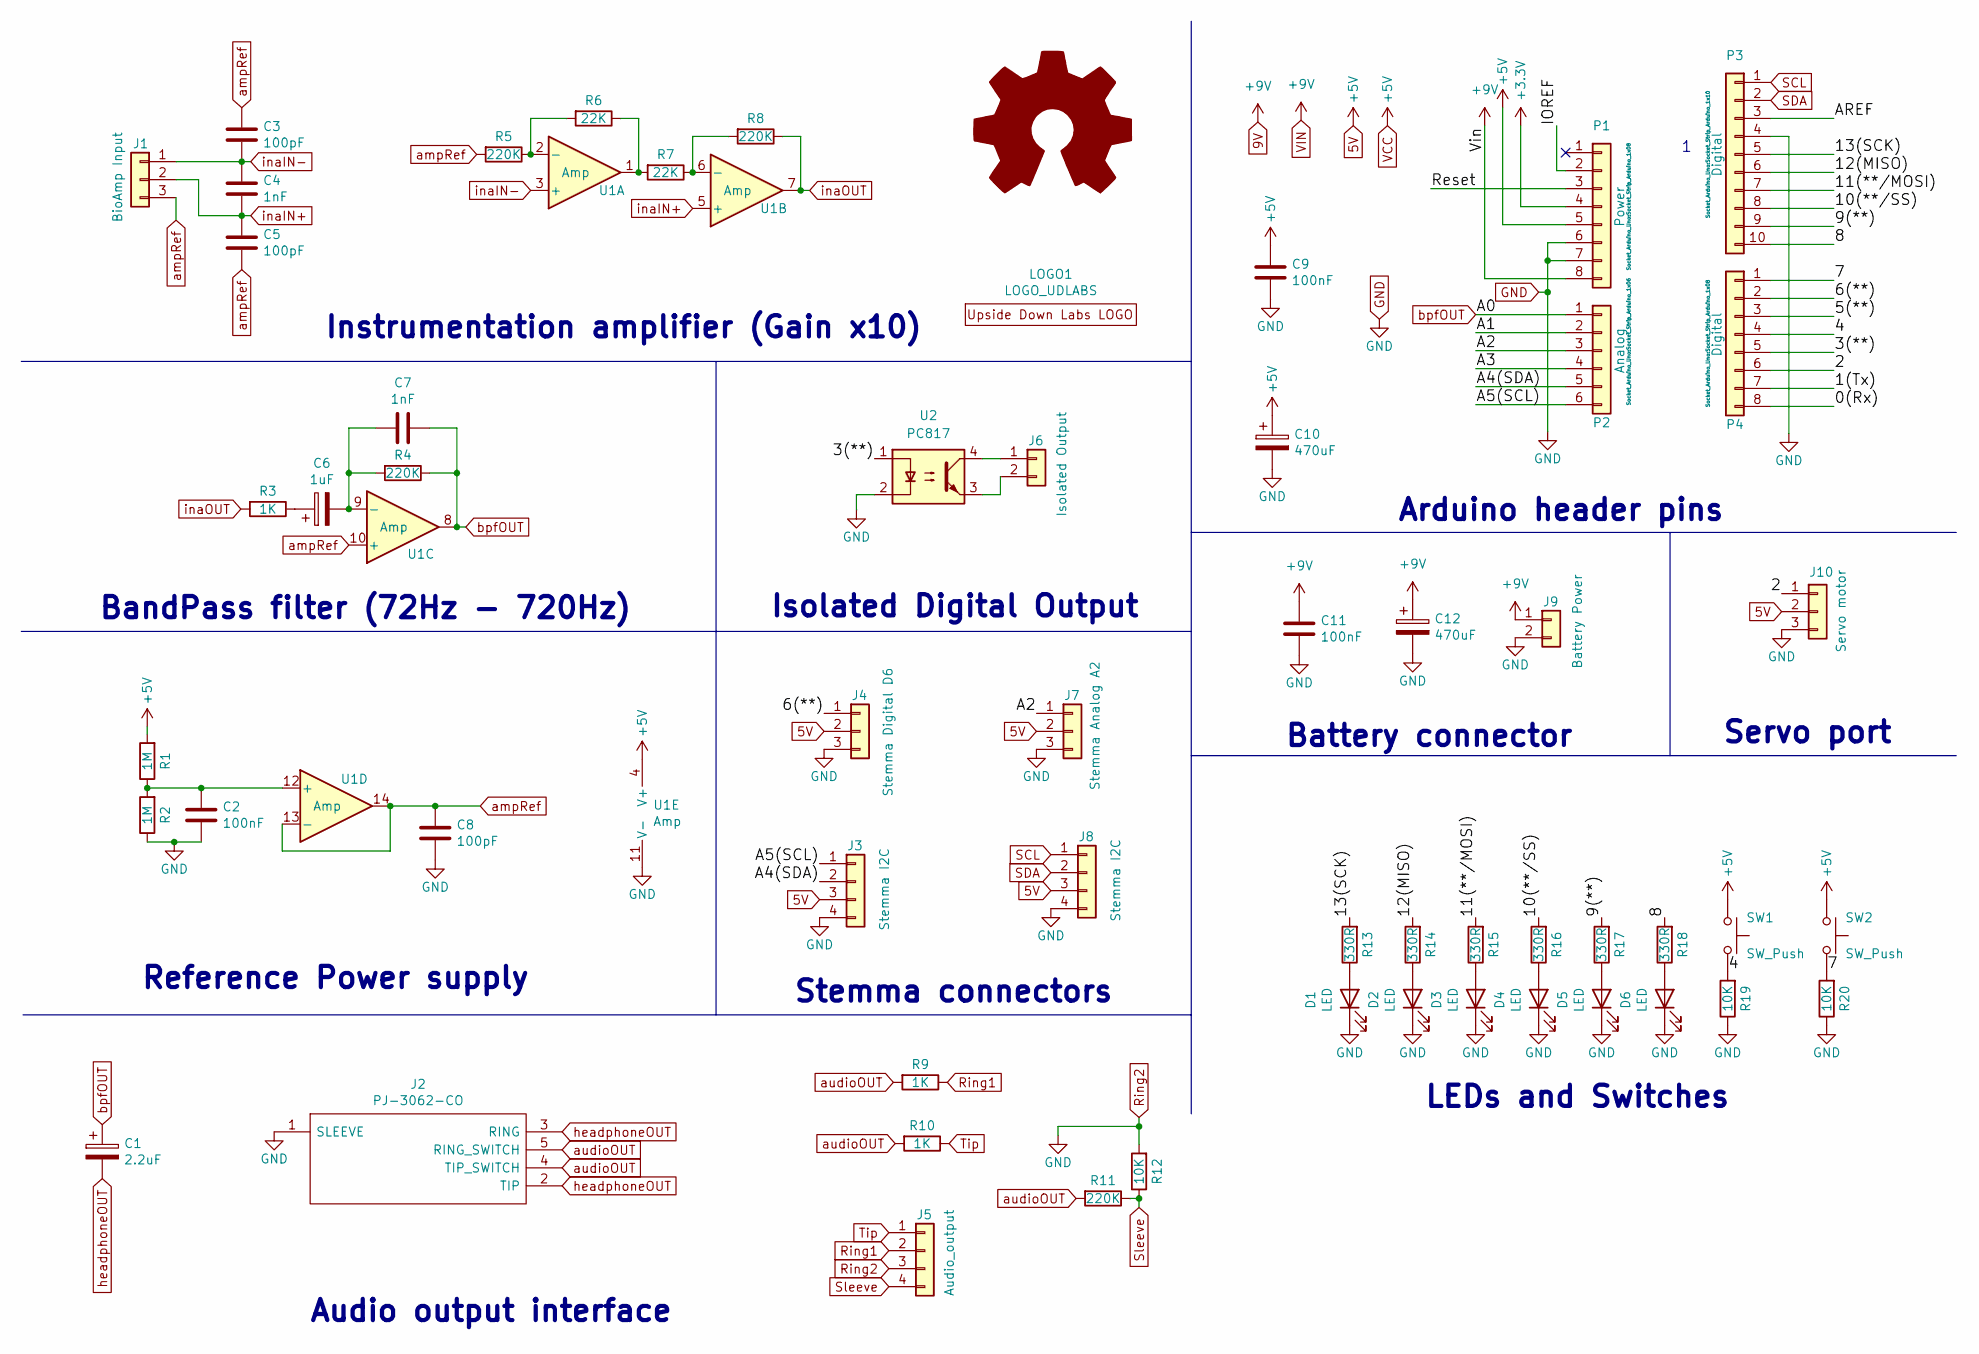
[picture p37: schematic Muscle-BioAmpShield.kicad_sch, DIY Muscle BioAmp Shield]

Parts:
C1: 2.2uF; CP_Radial_D5.0mm_P2.50mm
C2, C9, C11: 100nF; C_Disc_D3.8mm_W2.6mm_P2.50mm
C3, C5, C8: 100pF; C_Disc_D3.8mm_W2.6mm_P2.50mm
C4, C7: 1nF; C_Disc_D3.8mm_W2.6mm_P2.50mm
C6: 1uF; CP_Radial_D5.0mm_P2.50mm
C10, C12: 470uF; CP_Radial_D5.0mm_P2.50mm
D1, D2, D3, D4, D5, D6: LED; LED_D5.0mm
J1: BioAmp Input; JST_PH_S3B-PH-K_1x03_P2.00mm_Horizontal
J2: PJ-3062-CO; PJ3062CO; Manufacturer_Part_Number PJ-3062-CO
J3: Stemma I2C; JST_PH_B4B-PH-K_1x04_P2.00mm_Vertical
J4: Stemma Digital D6; JST_PH_B3B-PH-K_1x03_P2.00mm_Vertical
J5: Audio_output; JST_PH_S4B-PH-K_1x04_P2.00mm_Horizontal
J6: Isolated Output; JST_PH_B2B-PH-K_1x02_P2.00mm_Vertical
J7: Stemma Analog A2; JST_PH_B3B-PH-K_1x03_P2.00mm_Vertical
J8: Stemma I2C; JST_PH_S4B-PH-K_1x04_P2.00mm_Horizontal
J9: Battery Power; JST_PH_S2B-PH-K_1x02_P2.00mm_Horizontal
J10: Servo motor; PinHeader_1x03_P2.54mm_Vertical
LOGO1: LOGO_UDLABS; upsidedownlabsLOGO_41x34
P1: Power; Socket_Strip_Arduino_1x08
P2: Analog; Socket_Strip_Arduino_1x06
P3: Digital; Socket_Strip_Arduino_1x10
P4: Digital; Socket_Strip_Arduino_1x08
R1, R2: 1M; R_Axial_DIN0207_L6.3mm_D2.5mm_P7.62mm_Horizontal
R3, R9, R10: 1K; R_Axial_DIN0207_L6.3mm_D2.5mm_P7.62mm_Horizontal
R4, R5, R8, R11: 220K; R_Axial_DIN0207_L6.3mm_D2.5mm_P7.62mm_Horizontal
R6, R7: 22K; R_Axial_DIN0207_L6.3mm_D2.5mm_P7.62mm_Horizontal
R12, R19, R20: 10K; R_Axial_DIN0207_L6.3mm_D2.5mm_P7.62mm_Horizontal
R13, R14, R15, R16, R17, R18: 330R; R_Axial_DIN0207_L6.3mm_D2.5mm_P7.62mm_Horizontal
SW1, SW2: SW_Push; SW_PUSH_6mm_H5mm
U1: Amp; DIP-14_W7.62mm_Socket_LongPads
U2: PC817; DIP-4_W7.62mm

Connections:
5V: C9.2, C10.1, J3.3, J4.2, J7.2, J8.3, J10.2, P1.5, R1.2, SW1.1, SW2.1, U1.4 (V+)
9V: C11.2, C12.1, J9.1, P1.8
+3V3: P1.4
/0(Rx): P4.8
/1(Tx): P4.7
/2: J10.1, P4.6
/3(**): P4.5, U2.1
/4: P4.4, R19.2, SW1.2
/5(**): P4.3
/6(**): J4.1, P4.2
/7: P4.1, R20.2, SW2.2
/8: P3.10, R18.2
/9(**): P3.9, R17.2
/10(**/SS): P3.8, R16.2
/11(**/MOSI): P3.7, R15.2
/12(MISO): P3.6, R14.2
/13(SCK): P3.5, R13.2
/A1: P2.2
/A2: J7.1, P2.3
/A3: P2.4
/A4(SDA): J3.2, P2.5
/A5(SCL): J3.1, P2.6
/AREF: P3.3
/IOREF: P1.2
/Reset: P1.3
GND: C2.1, C8.1, C9.1, C10.2, C11.1, C12.2, D1.1 (K), D2.1 (K), D3.1 (K), D4.1 (K), D5.1 (K), D6.1 (K), J2.1 (SLEEVE), J3.4, J4.3, J5.3, J7.3, J8.4, J9.2, J10.3, P1.6, P1.7, P3.4, R2.1, R12.2, R19.1, R20.1, U1.11 (V-), U2.2
unnamed: C2.2, R1.1, R2.2, U1.12 (+)
unnamed: C6.1, R3.1
unnamed: C6.2, C7.1, R4.2, U1.9 (-)
unnamed: D1.2 (A), R13.1
unnamed: D2.2 (A), R14.1
unnamed: D3.2 (A), R15.1
unnamed: D4.2 (A), R16.1
unnamed: D5.2 (A), R17.1
unnamed: D6.2 (A), R18.1
unnamed: J6.1, U2.4
unnamed: J6.2, U2.3
unnamed: R5.1, R6.2, U1.2 (-)
unnamed: R6.1, R7.2, U1.1
unnamed: R7.1, R8.2, U1.6 (-)
Ring1: J5.2, R9.1
SCL: J8.1, P3.1
SDA: J8.2, P3.2
Sleeve: J5.4, R11.1, R12.1
Tip: J5.1, R10.1
ampRef: C3.2, C5.1, C8.2, J1.3, R5.2, U1.10 (+), U1.13 (-), U1.14
audioOUT: J2.4 (TIP_SWITCH), J2.5 (RING_SWITCH), R9.2, R10.2, R11.2
bpfOUT: C1.1, C7.2, P2.1, R4.1, U1.8
headphoneOUT: C1.2, J2.2 (TIP), J2.3 (RING)
inaIN+: C4.1, C5.2, J1.2, U1.5 (+)
inaIN-: C3.1, C4.2, J1.1, U1.3 (+)
inaOUT: R3.2, R8.1, U1.7

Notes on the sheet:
BandPass filter (72Hz - 720Hz)
Stemma connectors
Arduino header pins
Battery connector
Reference Power supply
Isolated Digital Output
Servo port
Audio output interface
LEDs and Switches
Instrumentation amplifier (Gain x10)

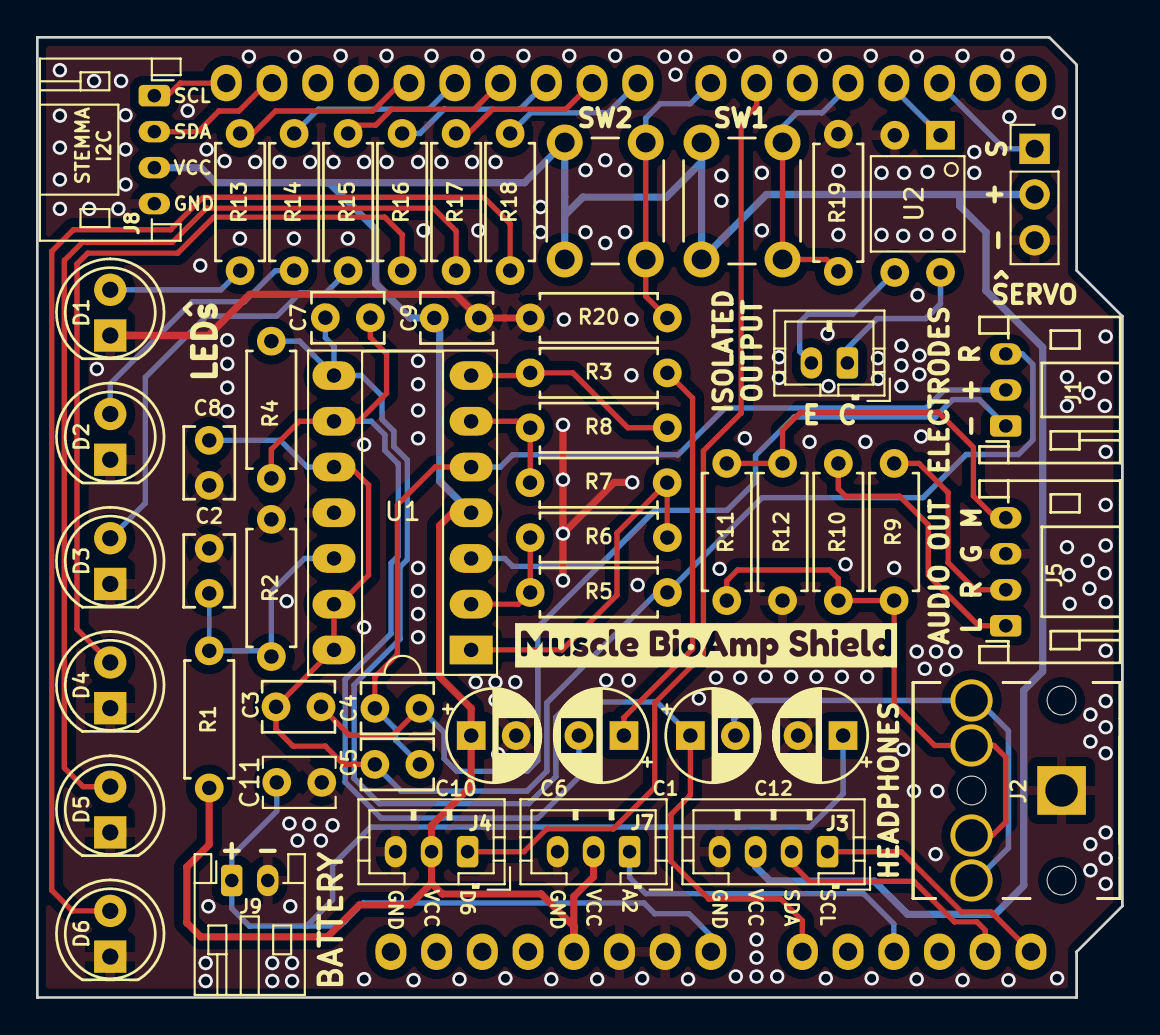
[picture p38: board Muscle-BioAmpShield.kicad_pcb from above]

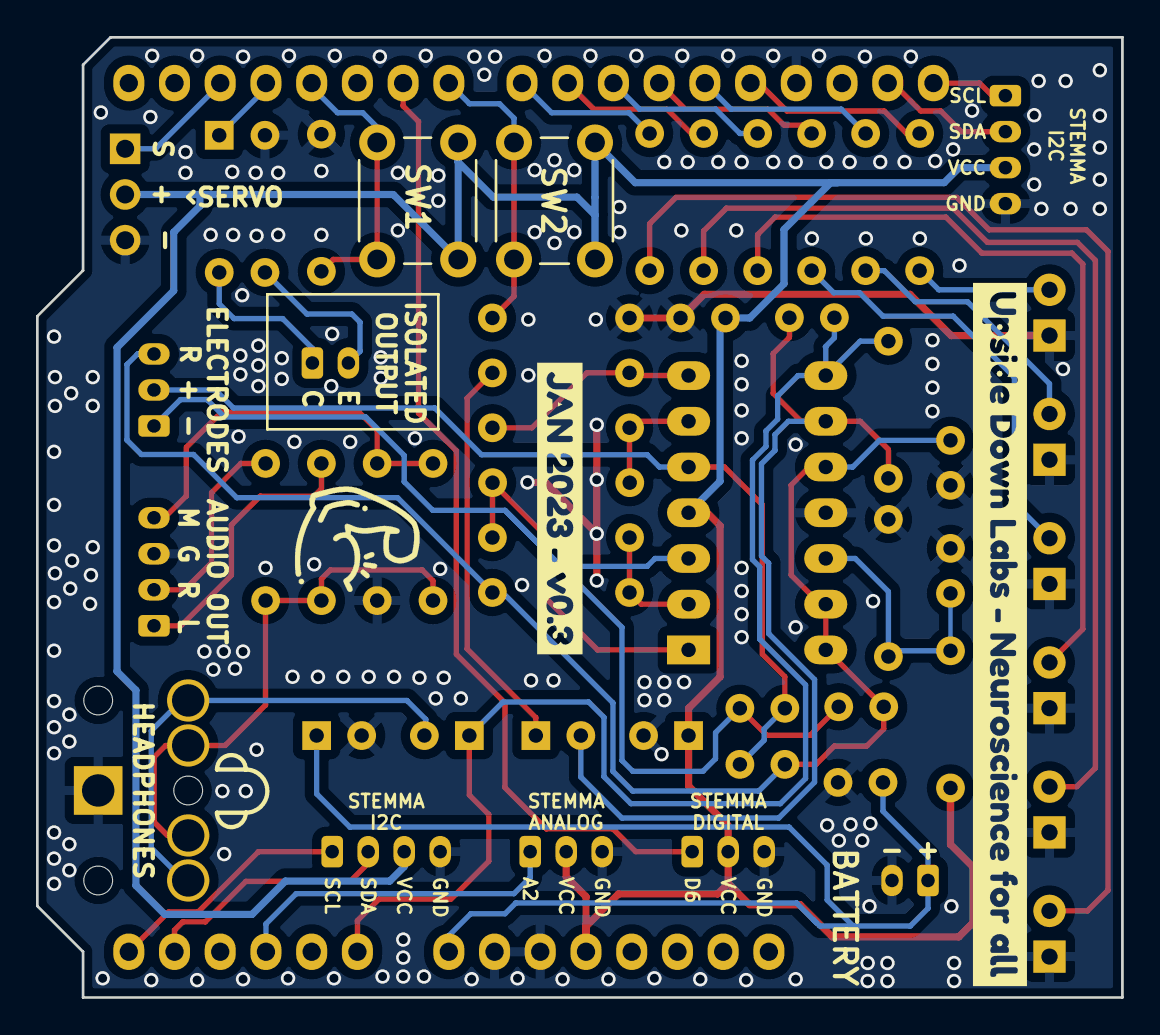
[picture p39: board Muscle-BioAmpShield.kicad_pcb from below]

Board: 2 copper layers, 60.3 x 53.3 mm, 59 parts (2 on the bottom side), 43 nets.

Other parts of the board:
kibuzzard-63B5E73F: G***; kibuzzard-63B5E73F
kibuzzard-63B67C69: G***; kibuzzard-63B67C69
kibuzzard-63B65023: G***; kibuzzard-63B65023

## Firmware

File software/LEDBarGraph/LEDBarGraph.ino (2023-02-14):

// LED Bar Graph - Muscle BioAmp Shield
// https://github.com/upsidedownlabs/Muscle-BioAmp-Shield

// Upside Down Labs invests time and resources providing this open source code,
// please support Upside Down Labs and open-source hardware by purchasing
// products from Upside Down Labs!

// Copyright (c) 2021-2022 Upside Down Labs - contact@upsidedownlabs.tech

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
#define SAMPLE_RATE 500
#define BAUD_RATE 115200
#define INPUT_PIN A0
#define BUFFER_SIZE 128

int circular_buffer[BUFFER_SIZE];
int data_index, sum;
// LED pin numbers in-order
int led_bar[] = {8, 9, 10, 11, 12, 13};
int total_leds = sizeof(led_bar) / sizeof(led_bar[0]);

void setup() {
	// Serial connection begin
	Serial.begin(BAUD_RATE);
	// Initialize all the led_bar
  	for (int i = 0; i < total_leds; i++) {
    	pinMode(led_bar[i], OUTPUT);
  	}
}

void loop() {
	// Calculate elapsed time
	static unsigned long past = 0;
	unsigned long present = micros();
	unsigned long interval = present - past;
	past = present;

	// Run timer
	static long timer = 0;
	timer -= interval;

	// Sample and get envelop
	if(timer < 0) {
		timer += 1000000 / SAMPLE_RATE;
		int sensor_value = analogRead(INPUT_PIN);
		int signal = EMGFilter(sensor_value);
		int envelop = getEnvelop(abs(signal));

		// Update LED bar graph
    	for(int i = 0; i<=total_leds; i++){
    		if(i>(envelop/4 - 14)){
      			digitalWrite(led_bar[i], LOW);
    		} else {
      			digitalWrite(led_bar[i], HIGH);
    		}
  		}

//		Serial.print(signal);
//		Serial.print(",");
		Serial.println(envelop);
	}
}

// Envelop detection algorithm
int getEnvelop(int abs_emg){
	sum -= circular_buffer[data_index];
	sum += abs_emg;
	circular_buffer[data_index] = abs_emg;
	data_index = (data_index + 1) % BUFFER_SIZE;
	return (sum/BUFFER_SIZE) * 2;
}

// Band-Pass Butterworth IIR digital filter, generated using filter_gen.py.
// Sampling rate: 500.0 Hz, frequency: [74.5, 149.5] Hz.
// Filter is order 4, implemented as second-order sections (biquads).
// Reference: 
// https://docs.scipy.org/doc/scipy/reference/generated/scipy.signal.butter.html
// https://courses.ideate.cmu.edu/16-223/f2020/Arduino/FilterDemos/filter_gen.py
float EMGFilter(float input)
{
  float output = input;
  {
    static float z1, z2; // filter section state
    float x = output - 0.05159732*z1 - 0.36347401*z2;
    output = 0.01856301*x + 0.03712602*z1 + 0.01856301*z2;
    z2 = z1;
    z1 = x;
  }
  {
    static float z1, z2; // filter section state
    float x = output - -0.53945795*z1 - 0.39764934*z2;
    output = 1.00000000*x + -2.00000000*z1 + 1.00000000*z2;
    z2 = z1;
    z1 = x;
  }
  {
    static float z1, z2; // filter section state
    float x = output - 0.47319594*z1 - 0.70744137*z2;
    output = 1.00000000*x + 2.00000000*z1 + 1.00000000*z2;
    z2 = z1;
    z1 = x;
  }
  {
    static float z1, z2; // filter section state
    float x = output - -1.00211112*z1 - 0.74520226*z2;
    output = 1.00000000*x + -2.00000000*z1 + 1.00000000*z2;
    z2 = z1;
    z1 = x;
  }
  return output;
}

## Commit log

2022-03-09 Muscle BioAmp Shield kicad files
    [BioAmpShield.kicad_pcb, BioAmpShield.sch, BioAmpShield_update.sch]
2022-06-08 LED bar graph software
2022-06-08 Update information
    [BioAmpShield.kicad_pcb, BioAmpShield.kicad_sch]
2022-12-01 Update hardware
    [BioAmpShield.kicad_sch]
2022-12-26 Update final design
    [BioAmpShield.kicad_pcb, BioAmpShield.kicad_sch]
2023-01-02 Update v0.2 data
    [BioAmpShield.kicad_pcb, BioAmpShield.kicad_sch, BioAmpShield.sch, BioAmpShield_update.sch]
2023-01-02 Update hardware to v0.2
    [Muscle-BioAmpShield.kicad_pcb, Muscle-BioAmpShield.kicad_sch, Muscle-BioAmpShield.sch]
2023-01-02 Fix Arduino code spelling
2023-02-14 Update to v0.3 KiCad files
    [Muscle-BioAmpShield.kicad_pcb, Muscle-BioAmpShield.kicad_sch]
2023-02-14 Add prefix DIY
    [Muscle-BioAmpShield.kicad_pcb, Muscle-BioAmpShield.kicad_sch]
2023-02-27 Update Shield Assembly Guide (#2)
    * Update img shields
    Updated all the important links for shield v0.3
    * Update shield graphics
    Update shield v0.3 renders, svgs, text.
    Add detailed features and specifications.
    * Update shield tilted render
    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
2023-05-06 Fix SVG graphics (#3)
    * Update tilted render
    * Update tilted render
    * Update tilted renders
    * Update tilted render
    * Update Render files
    * Update Shield assembly guide
    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
2023-05-25 minor filled zone update
    [Muscle-BioAmpShield.kicad_pcb]
